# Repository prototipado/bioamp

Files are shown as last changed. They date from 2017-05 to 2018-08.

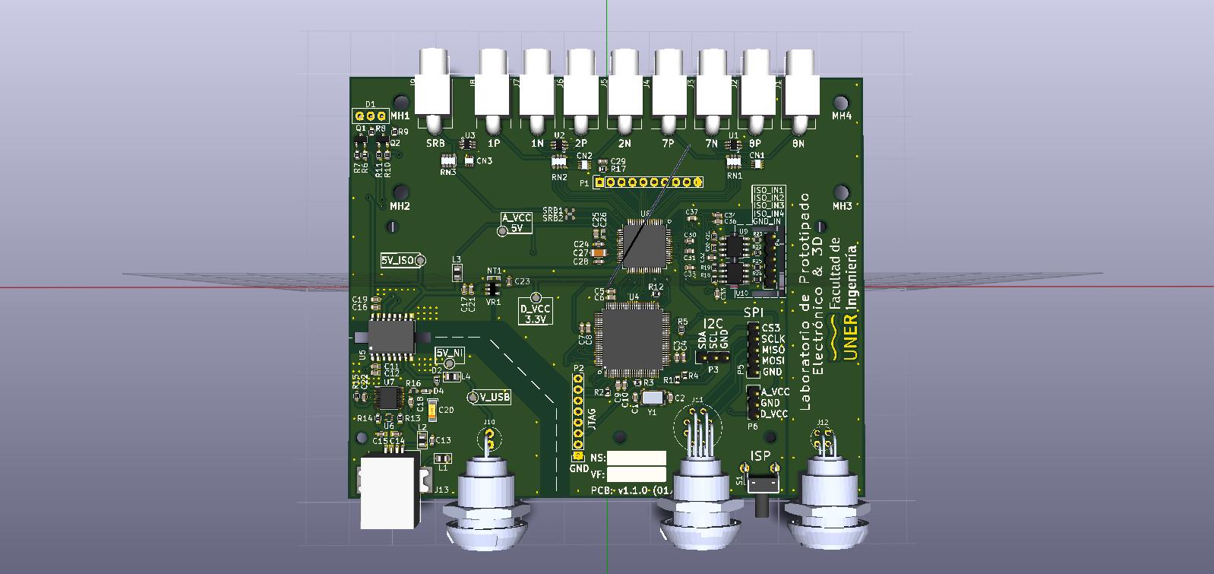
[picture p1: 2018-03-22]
Hardware/BioAmp_v1.1.0/images/BioAmp_v1.1.0_a.jpg

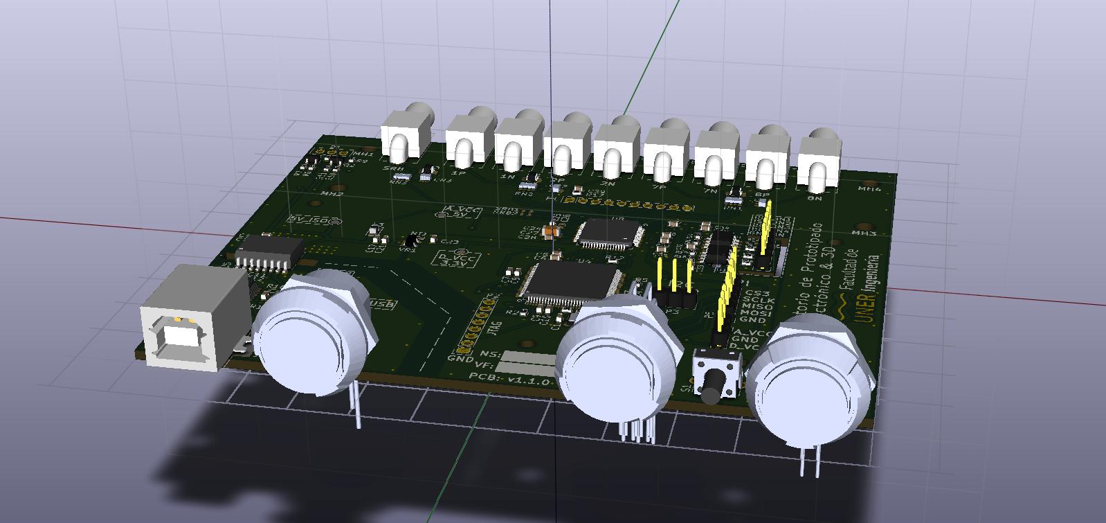
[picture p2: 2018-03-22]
Hardware/BioAmp_v1.1.0/images/BioAmp_v1.1.0_b.jpg

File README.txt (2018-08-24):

/****************************BioAmp Project**************************************************

Copyright 2017 - Laboratorio de Prototipado Electronico y 3D - FIUNER

Redistribution and use in source and binary forms, with or without modification, are permitted provided that the following conditions are met:

1. Redistributions of source code must retain the above copyright notice, this list of conditions and the following disclaimer.

2. Redistributions in binary form must reproduce the above copyright notice, this list of conditions and the following disclaimer in the documentation and/or other materials provided with the distribution.

3. Neither the name of the copyright holder nor the names of its contributors may be used to endorse or promote products derived from this design without specific prior written permission.

THIS DESING IS PROVIDED BY THE COPYRIGHT HOLDERS AND CONTRIBUTORS "AS IS" AND ANY EXPRESS OR IMPLIED WARRANTIES, INCLUDING, BUT NOT LIMITED TO, THE IMPLIED WARRANTIES OF MERCHANTABILITY AND FITNESS FOR A PARTICULAR PURPOSE ARE DISCLAIMED. IN NO EVENT SHALL THE COPYRIGHT HOLDER OR CONTRIBUTORS BE LIABLE FOR ANY DIRECT, INDIRECT, INCIDENTAL, SPECIAL, EXEMPLARY, OR CONSEQUENTIAL DAMAGES (INCLUDING, BUT NOT LIMITED TO, PROCUREMENT OF SUBSTITUTE GOODS OR SERVICES; LOSS OF USE, DATA, OR PROFITS; OR BUSINESS INTERRUPTION) HOWEVER CAUSED AND ON ANY THEORY OF LIABILITY, WHETHER IN CONTRACT, STRICT LIABILITY, OR TORT (INCLUDING NEGLIGENCE OR OTHERWISE) ARISING IN ANY WAY OUT OF THE USE OF THIS DESIGN, EVEN IF ADVISED OF THE POSSIBILITY OF SUCH DAMAGE.

/*
===============================================================================
 Initial Authors : 
		   Juan Ignacio Cerrudo (juanicerrudo@gmail.com) - Developer
		   Agustin Solano (asolano@gmail.com) - Developer
                   Eduardo Filomena (efilomena@ingenieria.uner.edu.ar) - Requirements Definition
		   Juan Manuel Reta (jmreta@ingenieria.uner.edu.ar ) - Project Manager
Colaborators:
		   Albano Peñalva (albanopenialva@gmail.com) - Developer
		   Christian Mista (cmista@ingenieria.uner.edu.ar) - Developer
===============================================================================
*/

BioAmp is an opensource project of a multichannel biopotential adquisition system for EEG, EMG, EOG and EOG signals.

The device has 8 programmable channels - 2000 Hz maximun sampling frequency, allowing the acquisition of biopotentials.

Features:

Resolution: 17 - 19 bits depending on settings (gain and sampling frequency).
Channels: 8 differential channels / 8 monopolar channels.
Input Impedance: ≥ 500 M Ω
Dimentions: 153x114x34mm

Laboratorio de Prototipado Electronico y 3D - FIUNER (http://ingenieria.uner.edu.ar/grupos/prototipado)
Laboratorio de Ingenierı́a en Rehabilitación e Investigaciones Neuromusculares y Sensoriales (LIRINS).

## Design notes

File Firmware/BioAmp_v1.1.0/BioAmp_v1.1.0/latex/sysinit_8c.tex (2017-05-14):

\hypertarget{sysinit_8c}{}\section{src/sysinit.c File Reference}
\label{sysinit_8c}\index{src/sysinit.\+c@{src/sysinit.\+c}}
{\ttfamily \#include \char`\"{}board.\+h\char`\"{}}\\*
\subsection*{Functions}
\begin{DoxyCompactItemize}
\item 
void \hyperlink{sysinit_8c_a93f514700ccf00d08dbdcff7f1224eb2}{System\+Init} (void)
\end{DoxyCompactItemize}

\subsection{Function Documentation}
\hypertarget{sysinit_8c_a93f514700ccf00d08dbdcff7f1224eb2}{}\index{sysinit.\+c@{sysinit.\+c}!System\+Init@{System\+Init}}
\index{System\+Init@{System\+Init}!sysinit.\+c@{sysinit.\+c}}
\subsubsection[{System\+Init(void)}]{\setlength{\rightskip}{0pt plus 5cm}void System\+Init (
\begin{DoxyParamCaption}
\item[{void}]{}
\end{DoxyParamCaption}
)}\label{sysinit_8c_a93f514700ccf00d08dbdcff7f1224eb2}

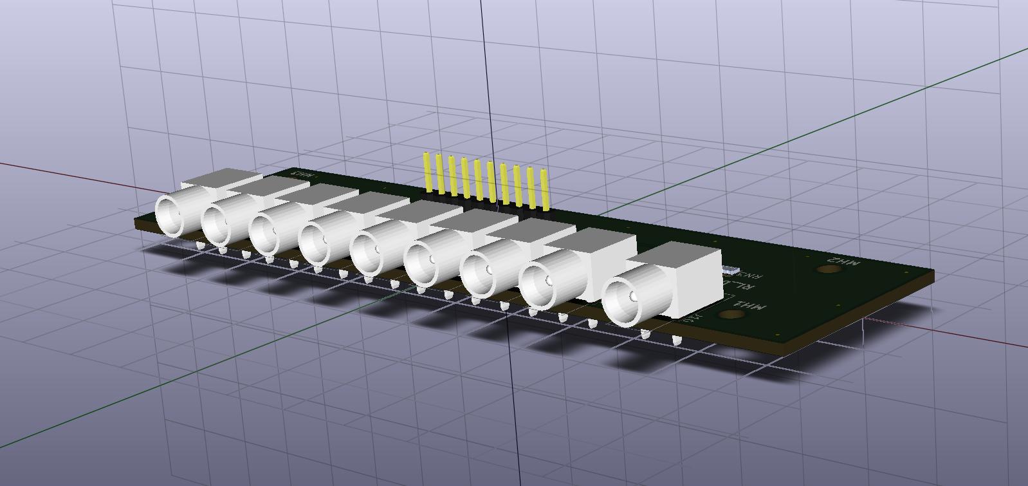
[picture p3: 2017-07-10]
Hardware/BioAmp_v1.1.0_DB/images/BioAmp_v1.0.0_DB_a.jpg

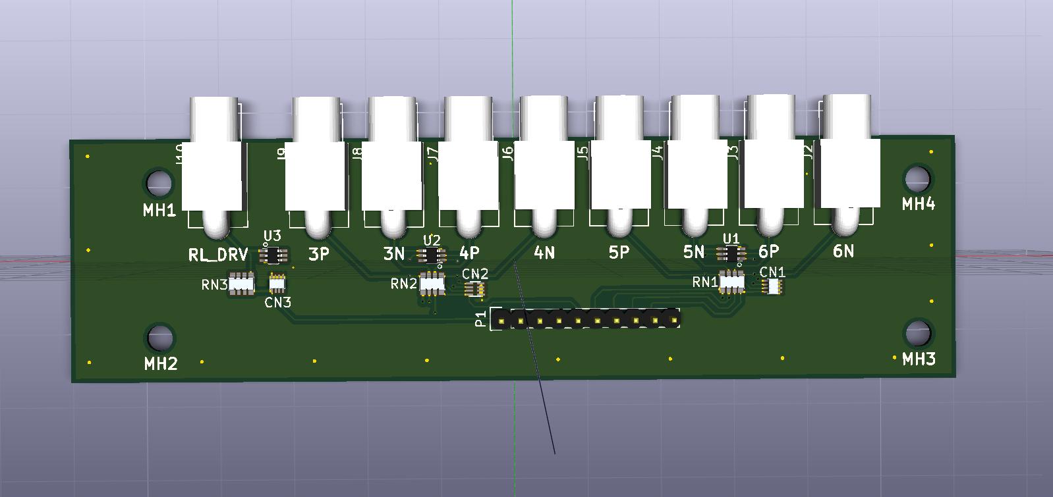
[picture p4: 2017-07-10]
Hardware/BioAmp_v1.1.0_DB/images/BioAmp_v1.0.0_DB_b.jpg

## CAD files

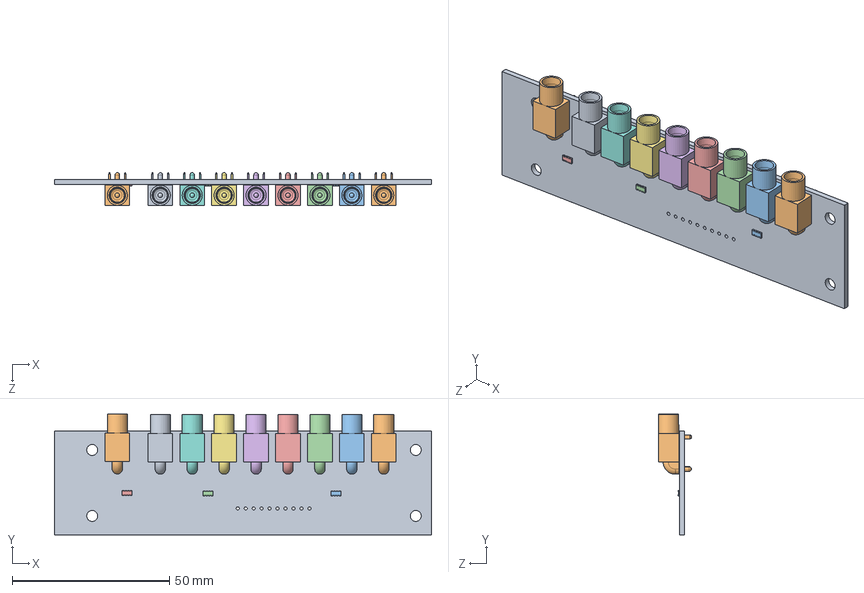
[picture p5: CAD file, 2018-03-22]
Hardware/3d_boards/BioAmp_v1.1.0_DB.SLDASM
120.0 x 38.4 x 10.4 mm
Board_outline_1
conector_touch-free__1
conector_touch-free_001_1
conector_touch-free_002_1
conector_touch-free_003_1
conector_touch-free_004_1
conector_touch-free_005_1
conector_touch-free_006_1
conector_touch-free_007_1
conector_touch-free_008_1
r_cay16-4__1
r_cay16-4_001_1
r_cay16-4_002_1

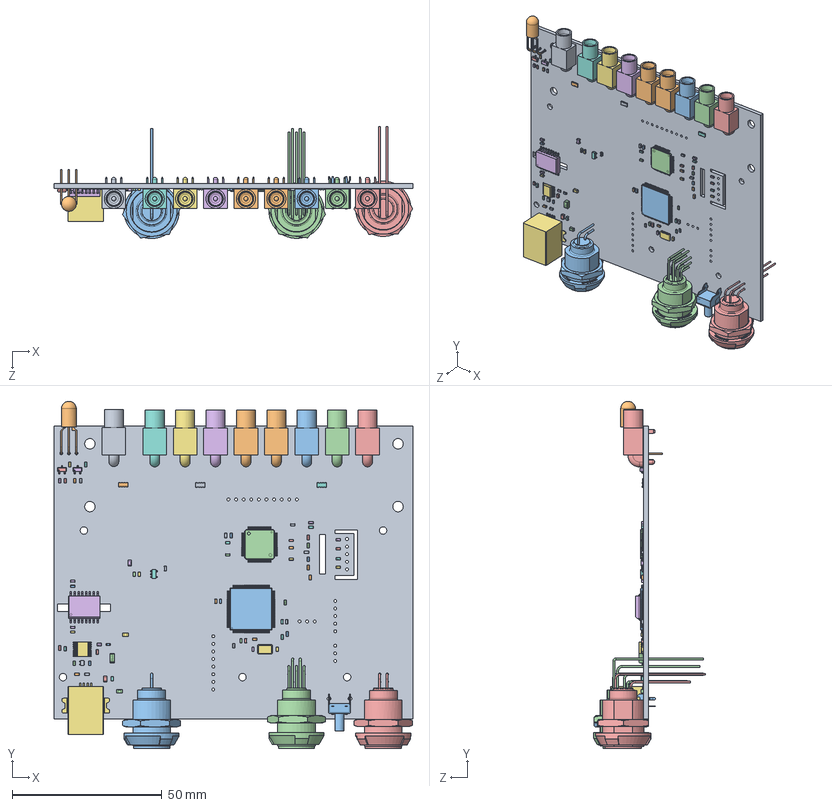
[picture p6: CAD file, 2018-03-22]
Hardware/3d_boards/BioAmp_v1.1.0.SLDASM
120.0 x 116.1 x 37.5 mm
Board_outline
conector_touch-free_
LQFP_100_14x14mm_Pitch0.5mm_
LQFP_64_10x10mm_Pitch0.5mm_
R_0603_
SOIC-16_7.5x10.3mm_Pitch1.27mm_
USB_B-smd_
C_0603_
C_0603_001
C_0603_002
C_0603_003
C_0603_004
C_0603_005
C_0603_006
C_0603_007
C_0603_008
C_0603_009
C_0603_010
C_0603_011
C_0603_012
C_0603_013
C_0603_014
C_0603_015
C_0603_016
C_0603_017
C_0603_018
C_0603_019
C_0603_020
C_0603_021
C_0603_022
C_0603_023
C_0603_024
C_0603_025
LED_TH_
LED_0603_
FER-0805_
FER-0805_001
FER-0805_002
FER-0805_003
R_0603_001
R_0603_002
R_0603_003
R_0603_004
R_0603_005
R_0603_006
R_0603_007
R_0603_008
R_0603_009
R_0603_010
R_0603_011
R_0603_012
R_0603_013
R_0603_014
R_0603_015
XTAL_AM3B_
r_cay16-4_
r_cay16-4_001
r_cay16-4_002
SW_Tactile_SPST_Angled_
c_tant_A_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

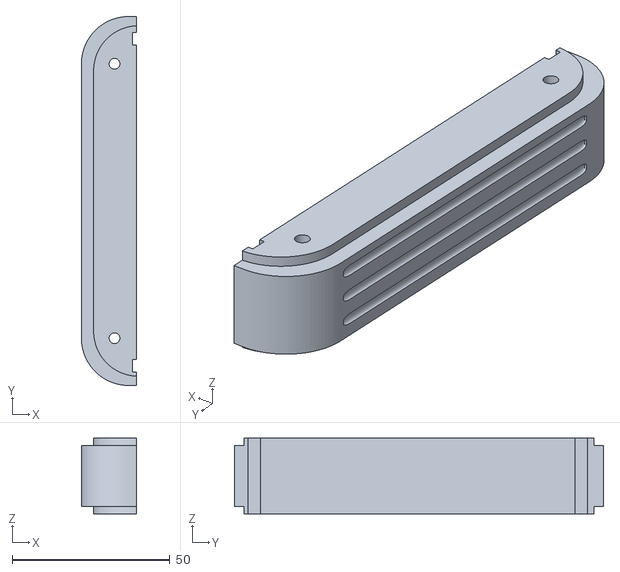
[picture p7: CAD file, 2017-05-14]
Enclosure/bioamp_body_right_1.0.stl
17.5 x 117.0 x 24.0

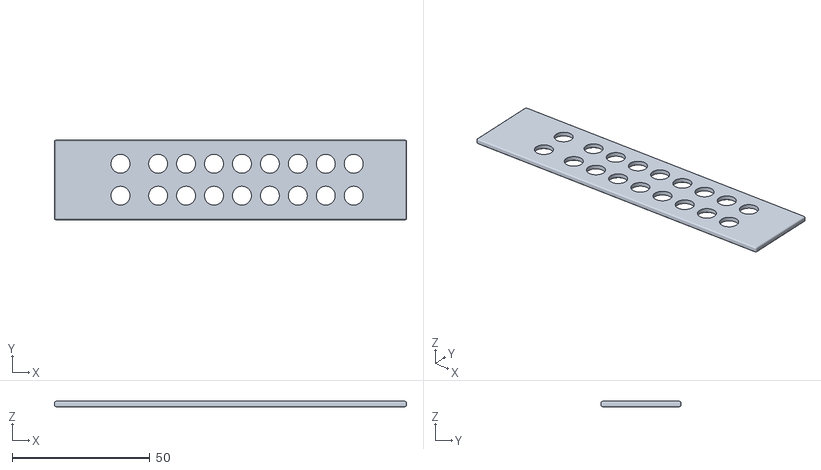
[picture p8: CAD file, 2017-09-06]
Enclosure/STL_1.2/bioamp_front_1.2.stl
128.0 x 29.0 x 2.00

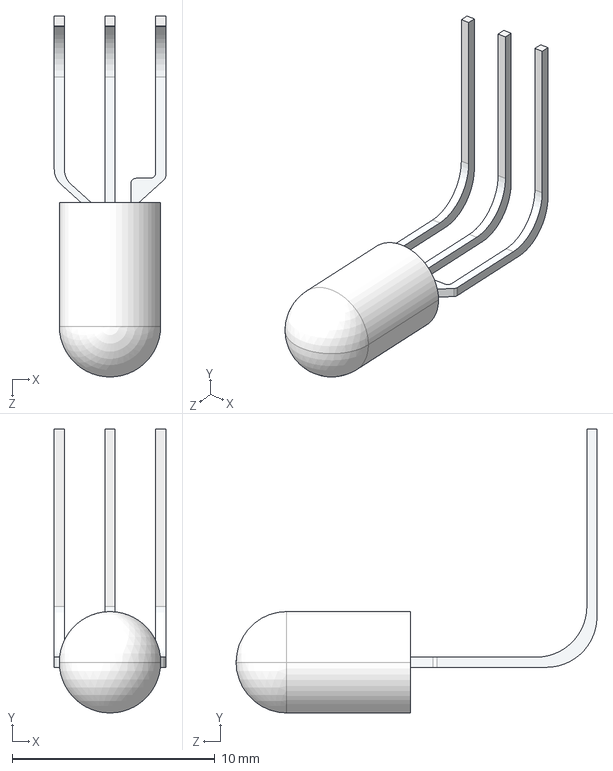
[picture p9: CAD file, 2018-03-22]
Hardware/BioAmp_v1.1.0/3d_models/LED_TH.STEP
5.50 x 14.0 x 17.8 mm

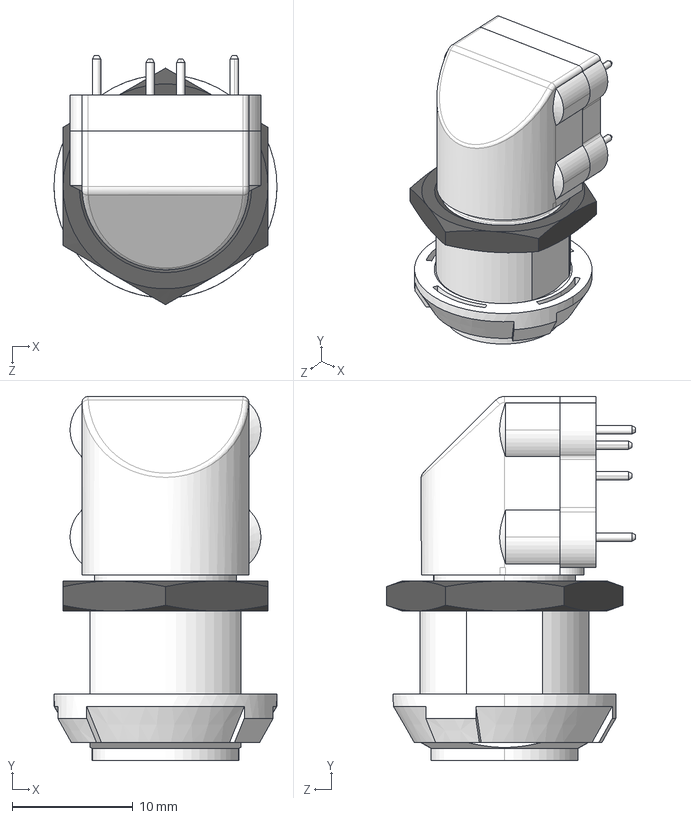
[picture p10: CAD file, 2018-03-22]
Hardware/BioAmp_v1.1.0_DB/3d_models/PXG.M0.4GG.NG.STEP
18.5 x 30.2 x 20.7 mm
pxg_m0_4gg_ng
pxg_m0_4gg_ng_2
pxg_m0_4gg_ng_3
pxg_m0_4gg_ng_4
pxg_m0_4gg_ng_5
pxg_m0_4gg_ng_6
pxg_m0_4gg_ng_7
pxg_m0_4gg_ng_8
pxg_m0_4gg_ng_9
pxg_m0_4gg_ng_10
pxg_m0_4gg_ng_11
pxg_m0_4gg_ng_12

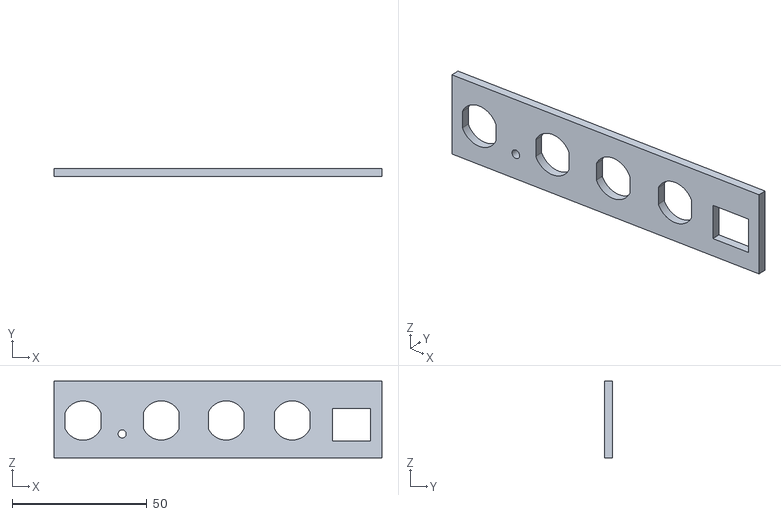
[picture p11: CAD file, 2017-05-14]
Enclosure/bioamp_back_1.0.stl
121.5 x 3.00 x 28.5

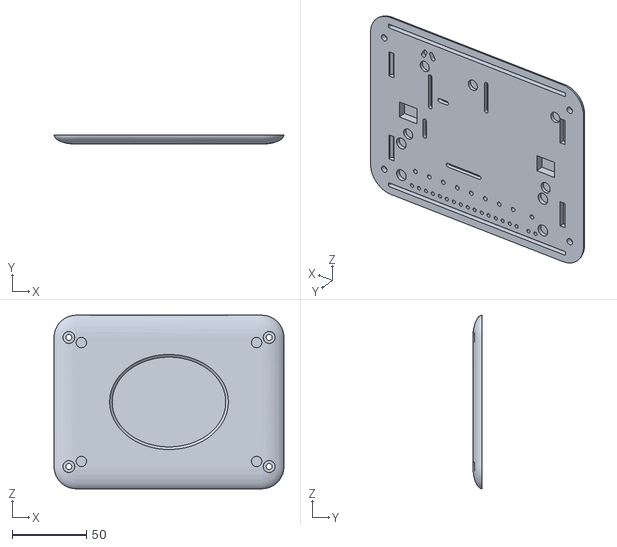
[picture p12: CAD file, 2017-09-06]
Enclosure/STL_1.2/bioamp_bottom_1.2.stl
155.0 x 6.25 x 117.0

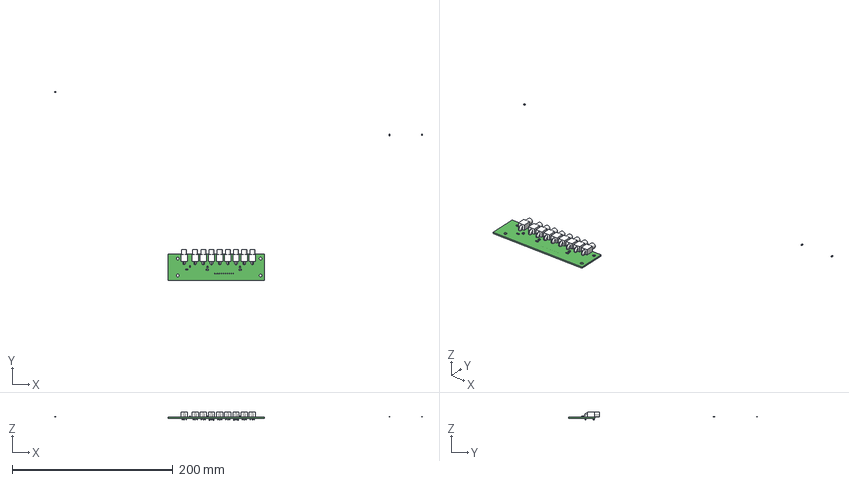
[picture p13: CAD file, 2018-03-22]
Hardware/3d_boards/BioAmp_v1_1_0_DB.FCStd
457.4 x 234.4 x 10.4 mm
Board_outline
r_cay16-4_
r_cay16-4_001
r_cay16-4_002
TSOP-6_2x1.25mm_Pitch0.65mm_
TSOP-6_2x1.25mm_Pitch0.65mm_001
Extruded_8_
Extruded_8_001
TSOP-6_2x1.25mm_Pitch0.65mm_002
Extruded_8_002
conector_touch-free_
conector_touch-free_001
conector_touch-free_002
conector_touch-free_003
conector_touch-free_004
conector_touch-free_005
conector_touch-free_006
conector_touch-free_007
conector_touch-free_008

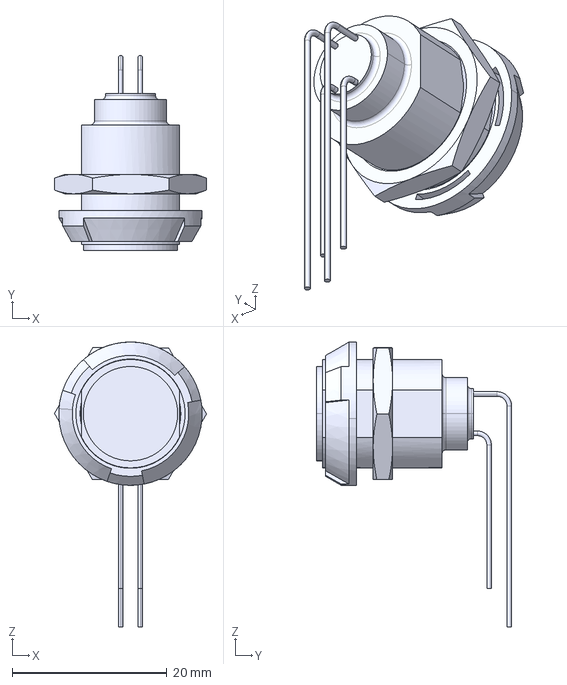
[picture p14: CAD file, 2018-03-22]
Hardware/BioAmp_v1.1.0/3d_models/PLB1G020004.step
19.6 x 25.2 x 36.8 mm

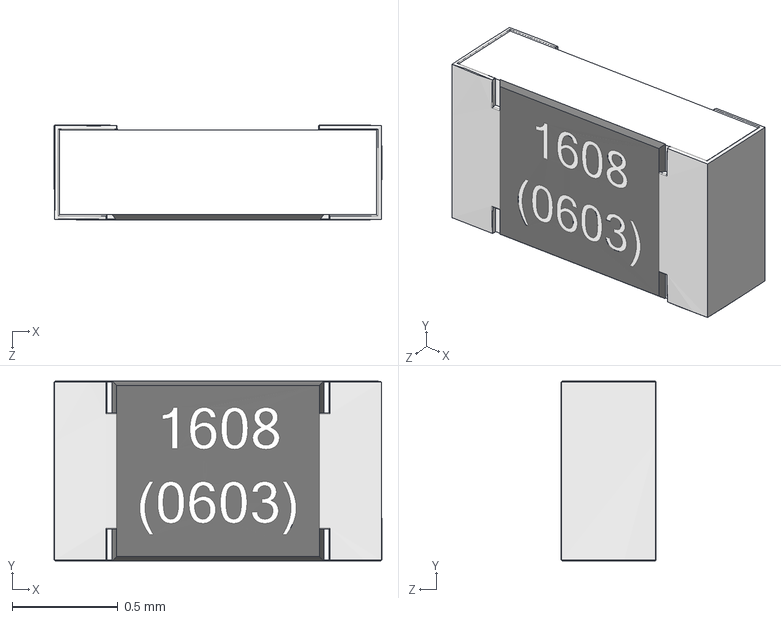
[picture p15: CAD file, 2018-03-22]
Hardware/BioAmp_v1.1.0_DB/3d_models/R_0603.STEP
1.55 x 0.85 x 0.451 mm

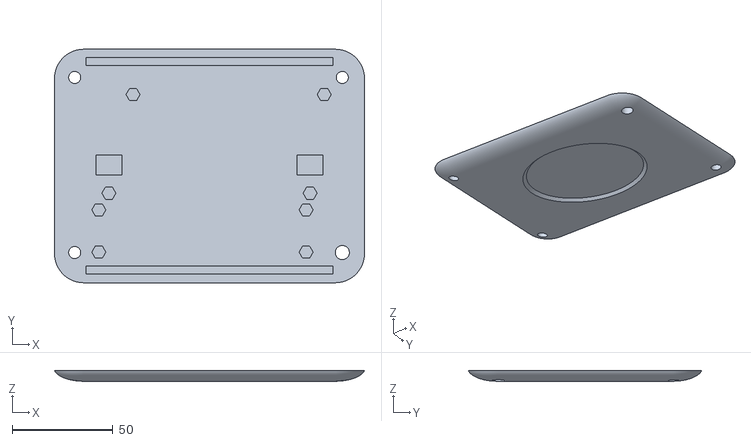
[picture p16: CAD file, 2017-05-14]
Enclosure/bioamp_bottom_1.0.stl
154.0 x 116.0 x 5.25

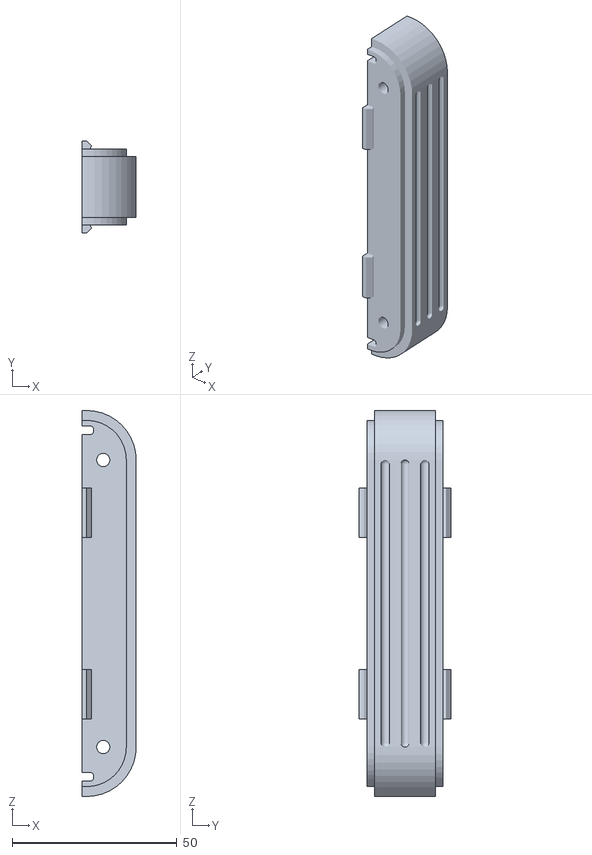
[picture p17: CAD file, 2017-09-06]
Enclosure/STL_1.2/bioamp_body_right_1.2.stl
16.5 x 28.0 x 117.0

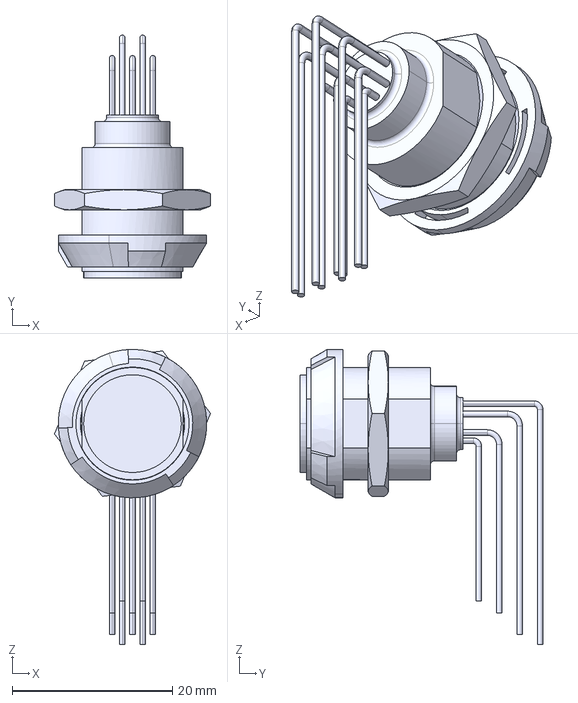
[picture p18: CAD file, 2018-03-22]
Hardware/BioAmp_v1.1.0/3d_models/PLB1G020010.step
19.5 x 30.3 x 36.8 mm

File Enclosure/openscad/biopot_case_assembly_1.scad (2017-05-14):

/**********************
Author: JM RETA
Project: Biopotencial Amplifier Case
Laboratorio de Prototipado Electrónico y 3D - FIUNER
02-2017

**********************/
//use <libs/nuts_and_bolts_v1.95.scad>;

$fn= 100;

/*Sphere  dimensions*/
X = 120;
Y = 75;
Z = 50;

sph_X = 100;
sph_Y = 80;
sph_Z = 60;
/*Dimension*/

X_i = 125;
Y_i = 85;//75
Z_i = 45;

/*Lateral Parameters*/

R_edges_v = 30; /*round radius for vertical edges*/
R_edges_h = 30; /*round radius for horizontal edges*/
thickness = 3;
/***Internal Hole***/

Xih = 120;
Yih = Y_i+R_edges_v;
Zih = 30;

/*******Grip Pattern*******/

G_DEEP = 0.3;
G_LONG = 80;
G_THICK = 1;
G_PITCH = 0.3;

/**************************/





/*Front panel*/
Xf = 120;
Yf = thickness-1;
Zf = 27;
R_border = 5;

border_thickness = 2.5;


/******Cuts**********/
Z_sph_cut =45;
Top_Part_Cut = R_edges_h/2-Z_i/2-3;
Bottom_Part_Cut = -R_edges_h/2-Z_i/2+3;
CUT = 1;
DRAW = 0;

/******Nuts Cuts*/
X_Border_Hole = 4.5;
Y_Border_Hole = 0;
Body_Nut_Heigth = 18;

/******Models***********/

sphere_top = 1;
boards_simulate = 0;
nuts_bolts=1;

GRIP_AND_CUTS = 1;

/*************************/
if(boards_simulate==1)
{
    color([0.3,0.8,0.5])
    {
        rotate([0,0,180])
        {
            translate([0,0,-9]) import("board.stl");
            translate([0,33,3])import("daugther_board.stl");
        }
    }
}

module grip_cylindrical (x_size, y_size, deep, pitch)
{
 
    //for ( i = [0 : pitch : (y_size-deep)/pitch] )
    for ( i = [0 : pitch : y_size] )
    {
        rotate( [90, 0, 0])
        {
            translate([0, 2*deep*20*i, 0]) minkowski()
            {
                cylinder(r = deep,h=x_size);
            resize(newsize=[deep,3*deep,10*deep])sphere(r=deep);
            }
        }
    }
}

module lateral(xl,yl,zl,r_edge_v,r_edge_h)
{
       minkowski()
       {
            cube([xl,yl,zl/2],center = true);
            resize(newsize=[r_edge_v,r_edge_h,14]) sphere(r_edge_v);
        }
}
module lateral_border(xl,yl,z,r_edge_v,r_edge_h)
{
difference()
{
lateral(xl,yl,z,r_edge_v,r_edge_h);
scale([0.95,0.95,0.95]) 
{
 lateral(xl,yl,z,r_edge_v,r_edge_h);
}
/*solids for substraction*/

 translate([0,0,Z_i/2])cube([2*X,2*Y,Z_i],center=true);
 translate([0,0,-Z_i/2-border_thickness])cube([2*X,2*Y,Z_i],center=true);
 }

/******/
 }
 module top_part()
 {
union()
{
        difference()
  //intersection()   
        {  
          union()
          {
//                hull()
//              {  
              lateral(X_i, Y_i, Z_i,R_edges_v,R_edges_h);
                if(sphere_top==1)
                {
                  difference()
                    {
                        resize(newsize=[sph_X,sph_Y,sph_Z]) sphere(r=20);
                /*sphere cut*/
                        translate ([0,0,Z_sph_cut])cube([X,Y,Z], center = true);  
                    }
 //               }
            }
            }
                //translate([0,0,0])
                translate([0,0,Top_Part_Cut ])cube([2*X_i,2*Y_i,Z_i],center=true);  
                front_part(CUT);
                back_part(CUT);
        }
    }
}
module body_part()
{
    difference()
    {
        intersection()
        {
            difference()
            {
               lateral(X_i, Y_i, Z_i,R_edges_v,R_edges_h);
               translate([0,0,-Top_Part_Cut+1.7])          lateral_border(X_i, Y_i, Z_i,R_edges_v,R_edges_h);
               translate([0,0,Bottom_Part_Cut/2+7.6])lateral_border(X_i, Y_i, Z_i,R_edges_v,R_edges_h);
               translate([0,0,-1]) cube([Xih,Yih+20,Zih],center=true);
//               #translate([0,0,-1]) cube([X_i, Y_i+R_edges_v, Z_i],center=true);
            }
      translate([0,0,Top_Part_Cut])cube([2*X_i,2*Y_i,Z_i],center=true);
        }
        translate([0,0,Bottom_Part_Cut])cube([2*X_i,2*Y_i,Z_i],center=true); 
        
    translate ([-X_i/2-X_Border_Hole, -Y_i/2-Y_Border_Hole, -20]) cylinder(r=3,Body_Nut_Heigth,$fn=6);
    translate ([-X_i/2-X_Border_Hole, Y_i/2-Y_Border_Hole, -20]) cylinder(r=3,Body_Nut_Heigth,$fn=6);
    translate ([X_i/2-X_Border_Hole+8, -Y_i/2-Y_Border_Hole, -20]) cylinder(r=3,Body_Nut_Heigth,$fn=6);
    translate ([X_i/2-X_Border_Hole+8, Y_i/2-Y_Border_Hole, -20]) cylinder(r=3,Body_Nut_Heigth,$fn=6);
        
    if(GRIP_AND_CUTS == 1)
    {
            front_part(CUT);
            back_part(CUT);
           translate([-X_i/2-15,G_LONG/2,-5.5])grip_cylindrical (G_LONG, G_THICK, G_DEEP, G_PITCH);
            translate([X_i/2+15,G_LONG/2,-5.5])grip_cylindrical (G_LONG, G_THICK, G_DEEP, G_PITCH);
    }
   }
}
module bottom_part()
{
    X_Board_Hole1 = 57;
    Y_Board_Hole1 = 35;
    
    X_Board_Hole2 = -38;
    Y_Board_Hole2 = 35;
    
    X_Board_Hole3 = -50;
    Y_Board_Hole3 = -14;
    
    X_Board_Hole4 = 50;
    Y_Board_Hole4 = -14;
    
    Z_Board_Hole = -16;
    
    Board_Nut_Heigth = 3.5;
    
 difference()
    {
union()
    {
        intersection()
        {
                lateral(X_i, Y_i, Z_i,R_edges_v,R_edges_h);
            translate([0,0,Bottom_Part_Cut-1])cube([2*X_i,2*Y_i,Z_i],center=true);
        }    
    }
    /****Front and Back panels cuts************/
    
    front_part(CUT);
    back_part(CUT);
    
    
    /****Cuts screws side by side***/
      translate([0,0,-Z_i+8])top_part();
    translate ([-X_i/2-X_Border_Hole, -Y_i/2-Y_Border_Hole, -20]) cylinder(r=1.5,Body_Nut_Heigth);
    translate ([-X_i/2-X_Border_Hole, Y_i/2-Y_Border_Hole, -20]) cylinder(r=1.5,Body_Nut_Heigth);
    translate ([X_i/2-X_Border_Hole+8, -Y_i/2-Y_Border_Hole, -20]) cylinder(r=1.5,Body_Nut_Heigth);
    translate ([X_i/2-X_Border_Hole+8, Y_i/2-Y_Border_Hole, -20]) cylinder(r=1.5,Body_Nut_Heigth);
    
    /***Cuts screws heads**/
    translate([0,0,-Z_i+8])top_part();
    translate ([-X_i/2-X_Border_Hole, -Y_i/2-Y_Border_Hole, -20]) cylinder(r=3,h=Body_Nut_Heigth/3.5);
    translate ([-X_i/2-X_Border_Hole, Y_i/2-Y_Border_Hole, -20]) cylinder(r=3,h=Body_Nut_Heigth/3.5);
    translate ([X_i/2-X_Border_Hole+8, -Y_i/2-Y_Border_Hole, -20]) cylinder(r=3,h=Body_Nut_Heigth/3.5);
    translate ([X_i/2-X_Border_Hole+8, Y_i/2-Y_Border_Hole, -20]) cylinder(r=3,h=Body_Nut_Heigth/3.5);

        /*****Board Nuts Cuts******/

     translate ([X_Board_Hole1, Y_Board_Hole1, Z_Board_Hole]) cylinder(r=3,Board_Nut_Heigth,$fn=6);
     translate ([X_Board_Hole2, Y_Board_Hole2, Z_Board_Hole]) cylinder(r=3,Board_Nut_Heigth,$fn=6);
     translate ([X_Board_Hole3, Y_Board_Hole3, Z_Board_Hole]) cylinder(r=3,Board_Nut_Heigth,$fn=6);
     translate ([X_Board_Hole4, Y_Board_Hole4, Z_Board_Hole]) cylinder(r=3,Board_Nut_Heigth,$fn=6);
    }
}

module front_part(for_cut)
{  
    X_Hole1 = 44.8;
    X_Hole2 = 57;
    Y_Hole1 = 5.5;
     Y_Hole2 = -6.5;
    Z_Hole1 = 50;
    Z_Hole2 = 50;
    
    X_cover_led = 55;
    Y_cover_led = -3.5;
    Z_cover_led = 47.5;
    
   if(for_cut ==1)
         {
           translate ([0,-(Yih/2-Yf-R_border/2-1.7),0])
             minkowski(){
            cube([Xf,Yf-1.5,Zf-R_border+2],center = true);
            rotate([90,0,0])cylinder(r=R_border/2,Yf+1);
            }
         }else
         {
           difference(){
               union(){
           translate ([0,-(Yih/2-Yf-R_border/2-2),0])
           minkowski(){
           cube([Xf,Yf-1.9,Zf-R_border+1],center = true);
           rotate([90,0,0])cylinder(r=R_border/2,Yf+1);
         }
                    /*led cover*/    
           difference()
           {
                rotate([90,0,0]) translate([X_cover_led,Y_cover_led,Z_cover_led]) cylinder(r=5,h=4);
                rotate([90,0,0]) translate([X_cover_led,  Y_cover_led,Z_cover_led]) cylinder(r=2.6,h=5);
           }
       }
       
       #rotate([90,0,0]) translate([X_cover_led,  Y_cover_led,Z_cover_led-1]) cylinder(r=3.5,h=5);
       
           difference(){
           rotate([90,0,0]) translate([X_cover_led,Y_cover_led,Z_cover_led+5.5]) cylinder(r=3.5,h=4);
           rotate([90,0,0]) translate([X_cover_led,  Y_cover_led,Z_cover_led+5.5]) cylinder(r=2.7,h=4);
           }
           
        for(i=[0:7]) {
        rotate([90,0,0]) translate([-X_Hole1+i*10.16,-Y_Hole1,Z_Hole1]) cylinder(r=3.8,h=6);
        }
        rotate([90,0,0]) translate([-X_Hole1+8*10+4.8,-Y_Hole1,Z_Hole1]) cylinder(r=3.8,h=6);     
        for(j=[0:7]) {
      rotate([90,0,0]) translate([-X_Hole1+j*10.16,-Y_Hole2,Z_Hole2]) cylinder(r=3.8,h=6);
        }
      rotate([90,0,0]) translate([-X_Hole1+8*10+4.8,-Y_Hole2,Z_Hole1]) cylinder(r=3.8,h=6);
      /*led cover*/        
        }
     }
}
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

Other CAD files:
Hardware/BioAmp_v1.1.0_DB/3d_models/PXG.M0.2GG.NG.STEP
Enclosure/bioamp_body_left_1.0.stl
Enclosure/STL_1.2/bioamp_back_1.2.stl
Hardware/BioAmp_v1.1.0/3d_models/led_bicolor.step
Enclosure/STL_1.2/bioamp_body_left_1.2.stl
Enclosure/STL_1.2/bioamp_standoff.STL
Enclosure/STL_1.2/bioamp_top_1.2.STL
Enclosure/STL_1.2/bioamp_top_UNER_1.2.STL
Enclosure/bioamp_front_1.0.stl
Enclosure/bioamp_top_1.0.stl
Hardware/BioAmp_v1.1.0/3d_models/C_0603.STEP
Hardware/BioAmp_v1.1.0/3d_models/Cap_Array_4.STEP
Hardware/BioAmp_v1.1.0/3d_models/FER-0805.STEP
Hardware/BioAmp_v1.1.0/3d_models/Jack_TouchProof_1.5mm.STEP
Hardware/BioAmp_v1.1.0/3d_models/LED_0603.STEP
Hardware/BioAmp_v1.1.0/3d_models/PLB1G020002.STEP
Hardware/BioAmp_v1.1.0/3d_models/R_0603.STEP
Hardware/BioAmp_v1.1.0/3d_models/SOIC-16_7.5x10.3mm_Pitch1.27mm.STEP
Hardware/BioAmp_v1.1.0/3d_models/SOIC-8_3.9x4.9mm_Pitch1.27mm.step
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

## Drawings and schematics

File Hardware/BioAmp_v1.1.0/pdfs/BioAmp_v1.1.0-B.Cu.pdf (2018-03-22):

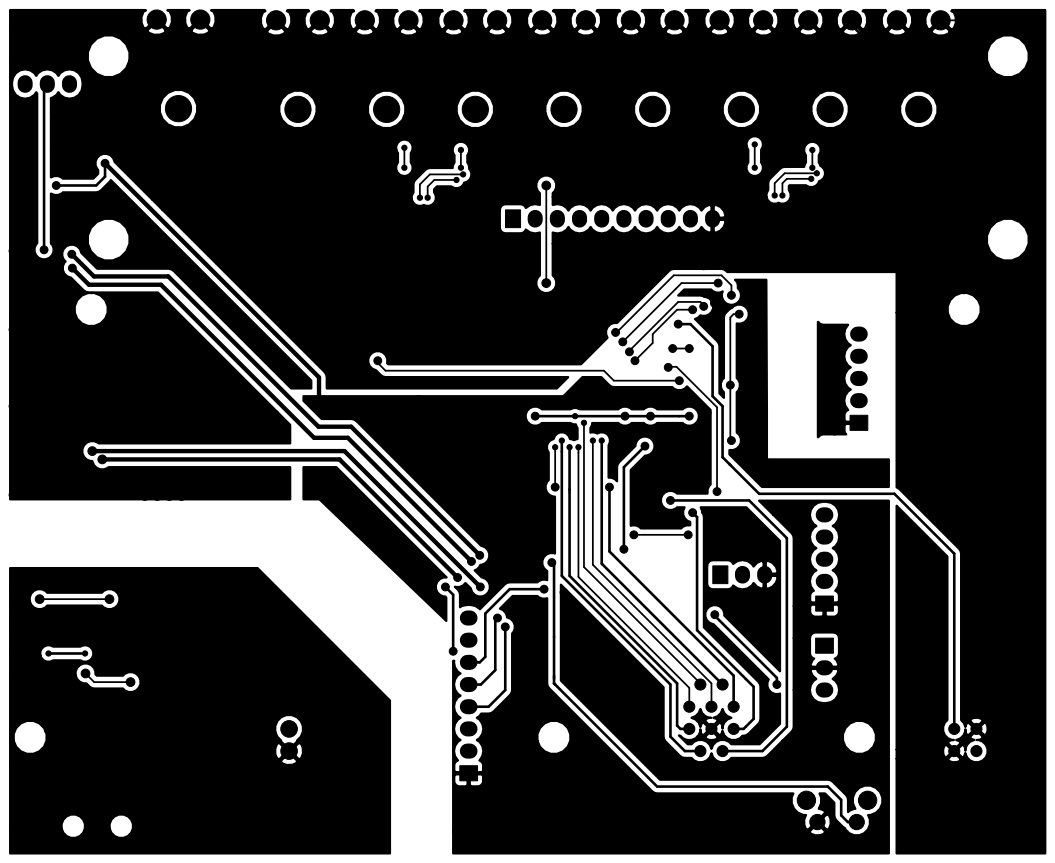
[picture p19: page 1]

File: BioAmp_v1.1.0.kicad_pcb Sheet:
Id: 1/1 Title: BioAmp-FIUNER-Lab. de Prototipado

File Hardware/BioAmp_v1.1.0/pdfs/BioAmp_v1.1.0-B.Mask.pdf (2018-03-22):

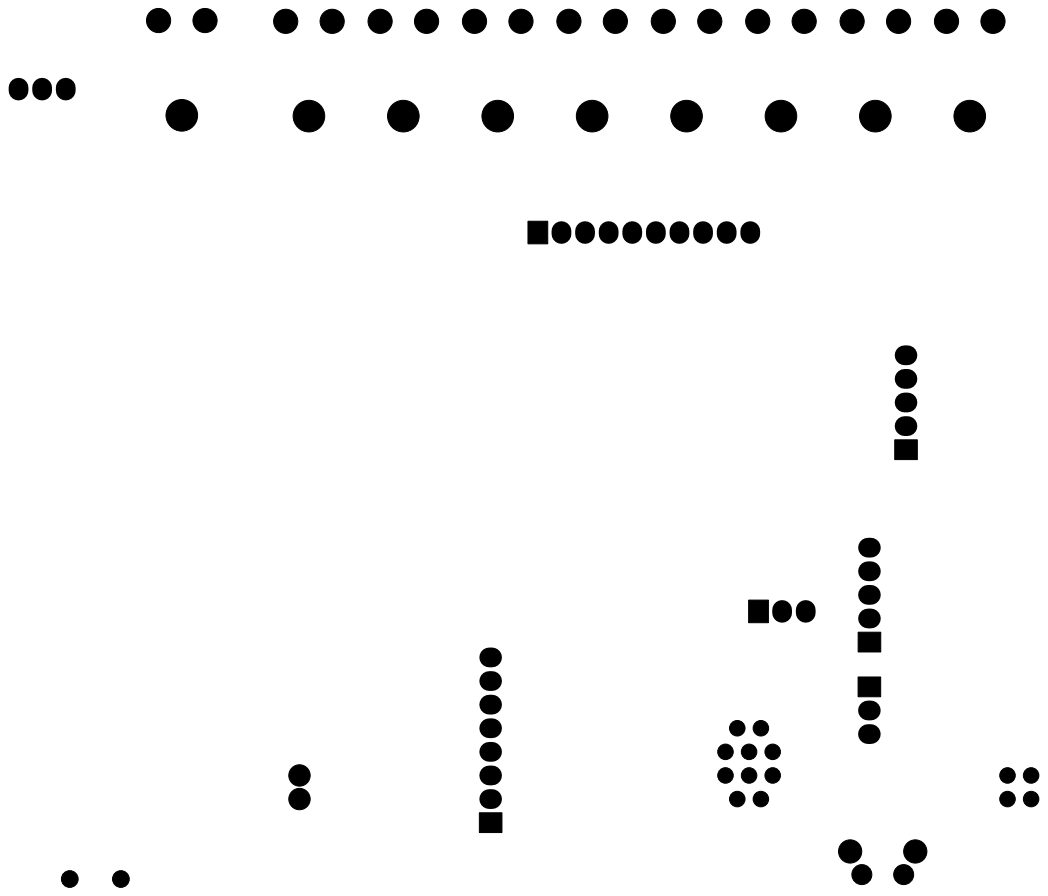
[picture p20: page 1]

File: BioAmp_v1.1.0.kicad_pcb Sheet:
Id: 1/1 Title: BioAmp-FIUNER-Lab. de Prototipado

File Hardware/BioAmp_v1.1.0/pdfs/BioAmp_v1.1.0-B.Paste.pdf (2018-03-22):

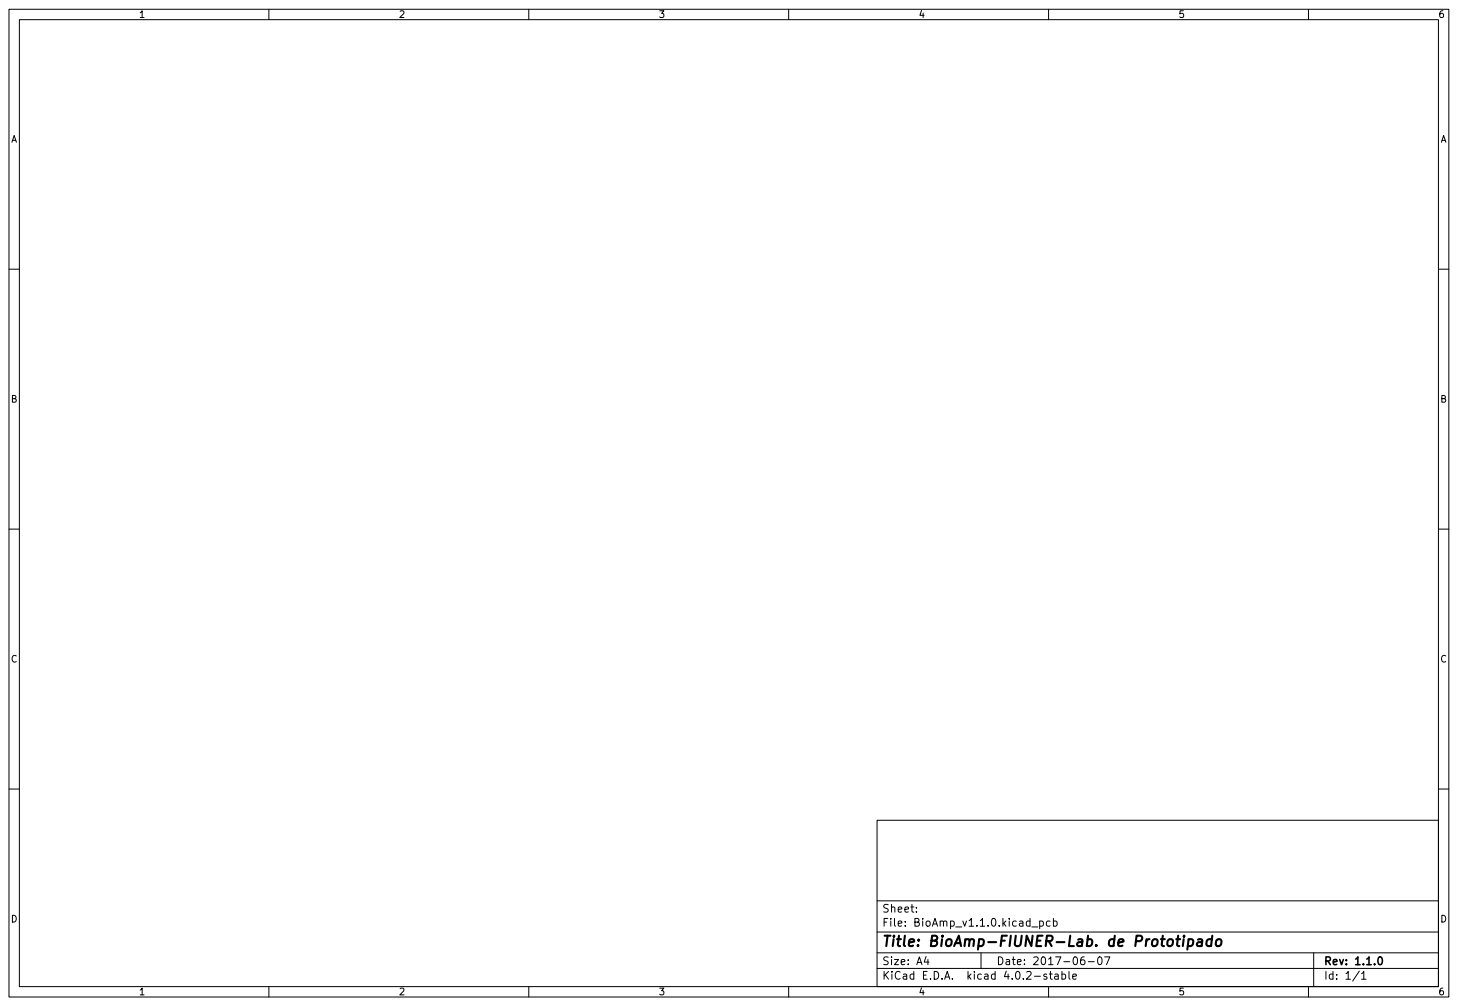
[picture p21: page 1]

File: BioAmp_v1.1.0.kicad_pcb Sheet:
Id: 1/1 Title: BioAmp-FIUNER-Lab. de Prototipado

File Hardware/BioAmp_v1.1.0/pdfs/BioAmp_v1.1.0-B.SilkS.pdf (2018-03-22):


File: BioAmp_v1.1.0.kicad_pcb Sheet:
Id: 1/1 Title: BioAmp-FIUNER-Lab. de Prototipado

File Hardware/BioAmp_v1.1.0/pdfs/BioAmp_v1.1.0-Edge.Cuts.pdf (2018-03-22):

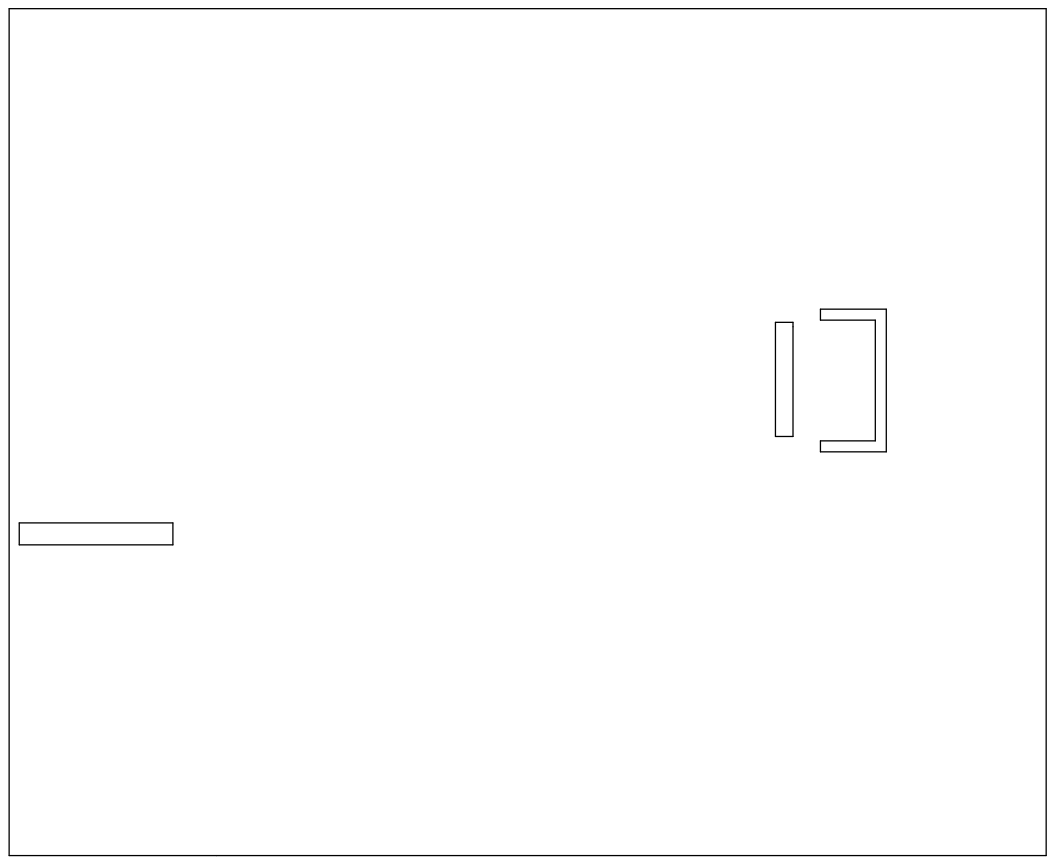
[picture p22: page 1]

File: BioAmp_v1.1.0.kicad_pcb Sheet:
Id: 1/1 Title: BioAmp-FIUNER-Lab. de Prototipado

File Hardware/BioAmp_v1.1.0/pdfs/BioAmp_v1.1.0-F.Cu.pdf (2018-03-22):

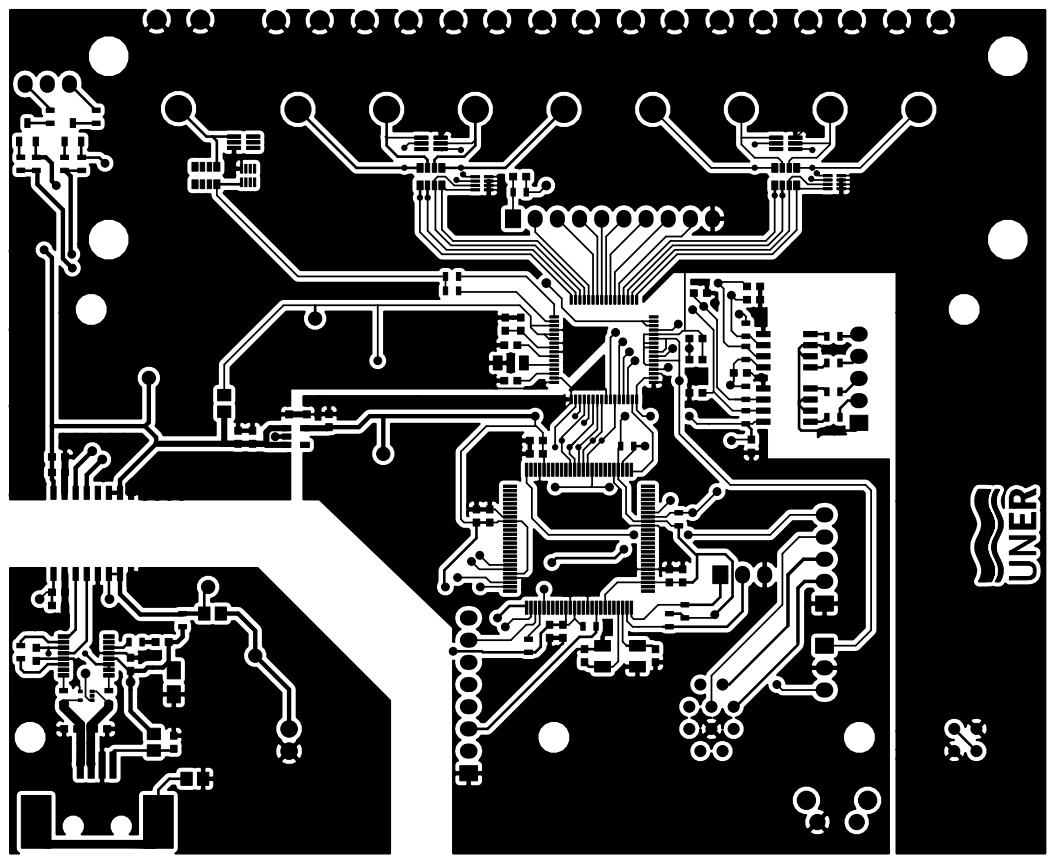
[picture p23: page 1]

File: BioAmp_v1.1.0.kicad_pcb Sheet:
Id: 1/1 Title: BioAmp-FIUNER-Lab. de Prototipado

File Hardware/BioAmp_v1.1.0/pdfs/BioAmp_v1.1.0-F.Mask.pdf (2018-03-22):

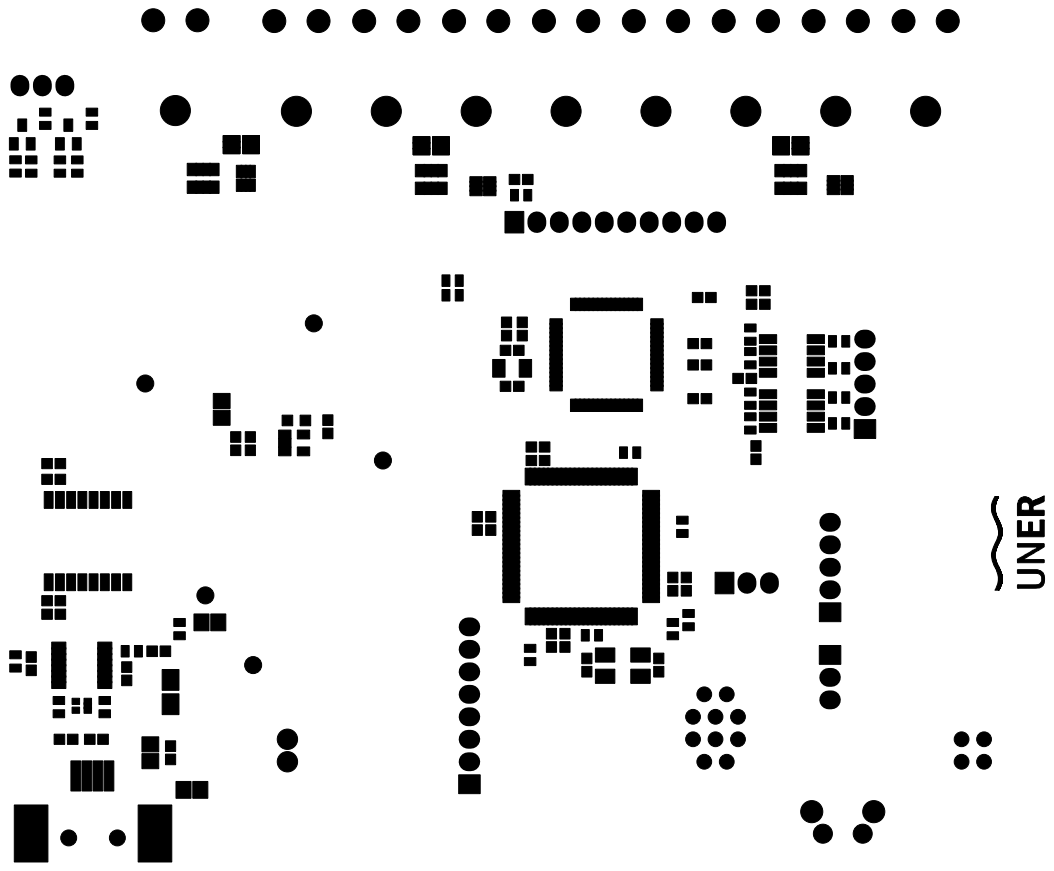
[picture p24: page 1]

File: BioAmp_v1.1.0.kicad_pcb Sheet:
Id: 1/1 Title: BioAmp-FIUNER-Lab. de Prototipado

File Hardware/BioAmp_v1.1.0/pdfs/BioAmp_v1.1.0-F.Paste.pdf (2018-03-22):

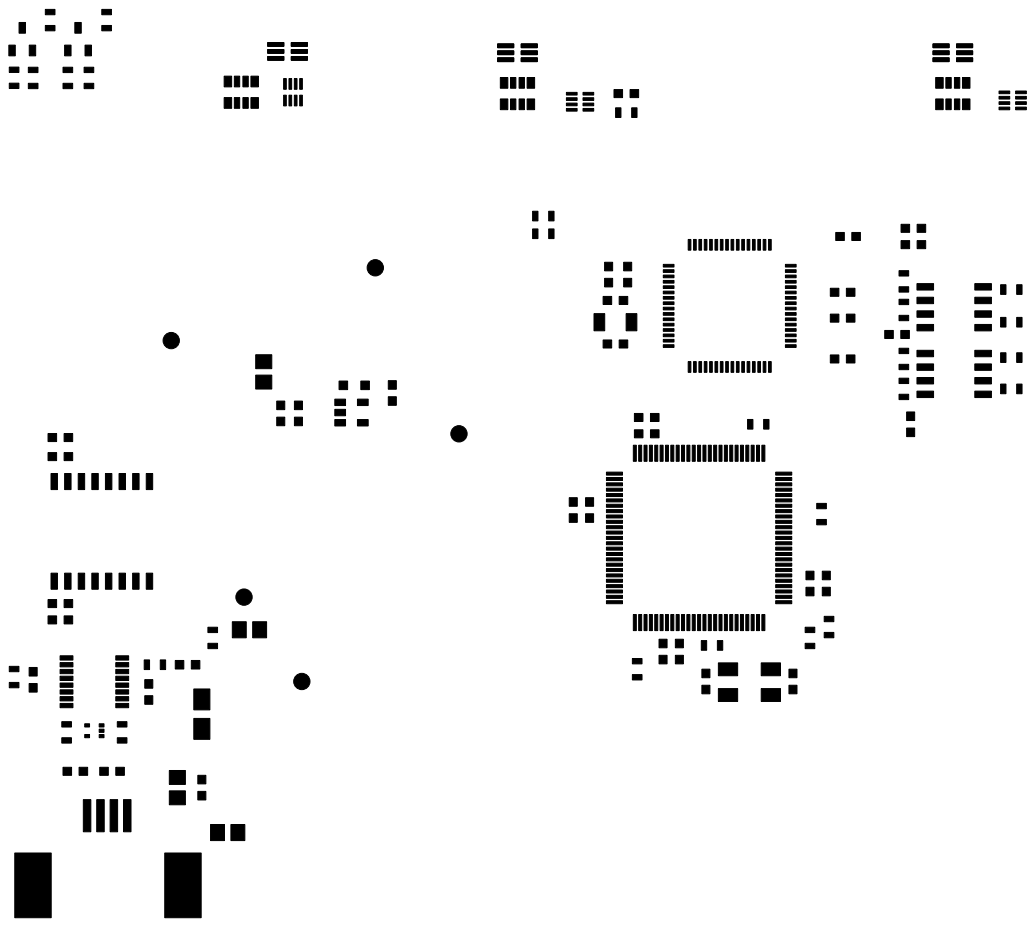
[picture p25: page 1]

File: BioAmp_v1.1.0.kicad_pcb Sheet:
Id: 1/1 Title: BioAmp-FIUNER-Lab. de Prototipado

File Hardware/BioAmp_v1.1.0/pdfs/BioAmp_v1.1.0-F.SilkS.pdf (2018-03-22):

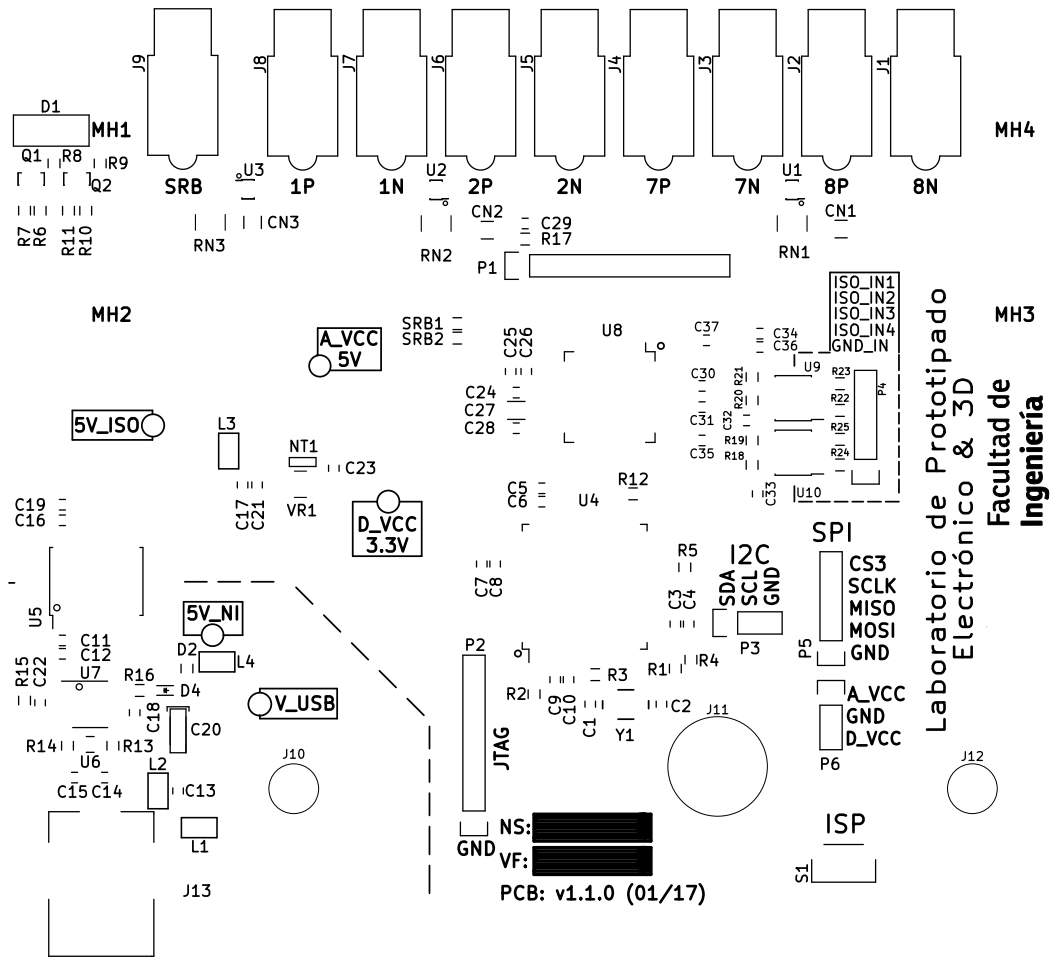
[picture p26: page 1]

CS3 SCLK MISO MOSI SDA SCL GND

Id: 1/1 Title: BioAmp-FIUNER-Lab. de Prototipado

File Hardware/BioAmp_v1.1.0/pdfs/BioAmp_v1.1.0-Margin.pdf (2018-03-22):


File: BioAmp_v1.1.0.kicad_pcb Sheet:
Id: 1/1 Title: BioAmp-FIUNER-Lab. de Prototipado

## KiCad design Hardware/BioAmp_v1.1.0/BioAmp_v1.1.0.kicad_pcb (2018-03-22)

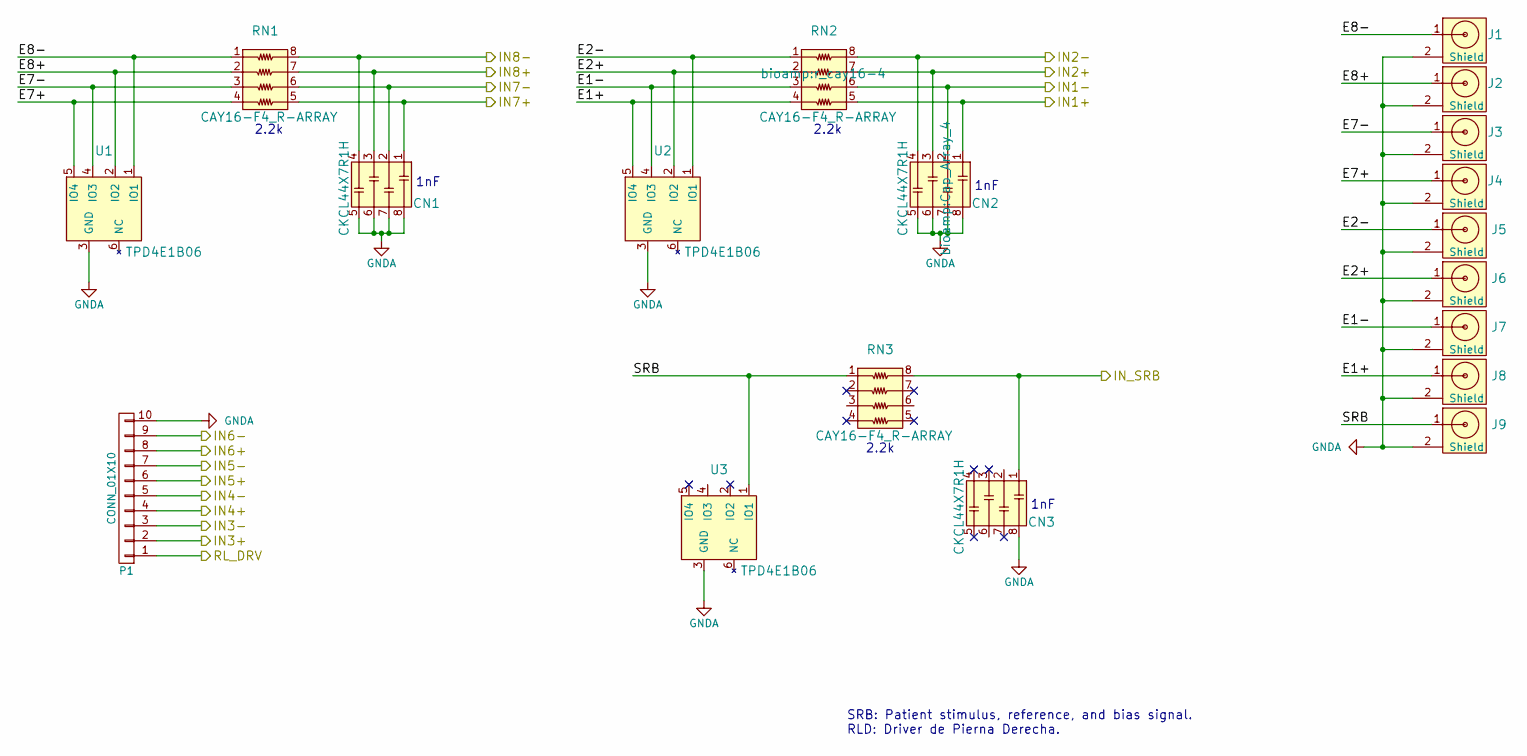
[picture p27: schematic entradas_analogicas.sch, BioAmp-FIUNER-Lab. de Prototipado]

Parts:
CN1, CN2, CN3: CKCL44X7R1H; Cap_Array_4
J1, J2, J3, J4, J5, J6, J7, J8, J9: Jack_Touch-Proof; Jack_TouchProof_1.5mm
P1: CONN_01X10; Pin_Header_Straight_1x10
RN1, RN2, RN3: CAY16-F4_R-ARRAY; r_cay16-4
U1, U2, U3: TPD4E1B06; TSOP-6_2x1.25mm_Pitch0.65mm

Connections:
/Analog Front End/RL_DRV: P1.1; also elsewhere on the board
/Entradas Analogicas/E1+: J8.1, RN2.4, U2.5 (IO4)
/Entradas Analogicas/E1-: J7.1, RN2.3, U2.4 (IO3)
/Entradas Analogicas/E2+: J6.1, RN2.2, U2.2 (IO2)
/Entradas Analogicas/E2-: J5.1, RN2.1, U2.1 (IO1)
/Entradas Analogicas/E7+: J4.1, RN1.4, U1.5 (IO4)
/Entradas Analogicas/E7-: J3.1, RN1.3, U1.4 (IO3)
/Entradas Analogicas/E8+: J2.1, RN1.2, U1.2 (IO2)
/Entradas Analogicas/E8-: J1.1, RN1.1, U1.1 (IO1)
/Entradas Analogicas/IN1+: CN2.1, RN2.5; also elsewhere on the board
/Entradas Analogicas/IN1-: CN2.2, RN2.6; also elsewhere on the board
/Entradas Analogicas/IN2+: CN2.3, RN2.7; also elsewhere on the board
/Entradas Analogicas/IN2-: CN2.4, RN2.8; also elsewhere on the board
/Entradas Analogicas/IN3+: P1.2; also elsewhere on the board
/Entradas Analogicas/IN3-: P1.3; also elsewhere on the board
/Entradas Analogicas/IN4+: P1.4; also elsewhere on the board
/Entradas Analogicas/IN4-: P1.5; also elsewhere on the board
/Entradas Analogicas/IN5+: P1.6; also elsewhere on the board
/Entradas Analogicas/IN5-: P1.7; also elsewhere on the board
/Entradas Analogicas/IN6+: P1.8; also elsewhere on the board
/Entradas Analogicas/IN6-: P1.9; also elsewhere on the board
/Entradas Analogicas/IN7+: CN1.1, RN1.5; also elsewhere on the board
/Entradas Analogicas/IN7-: CN1.2, RN1.6; also elsewhere on the board
/Entradas Analogicas/IN8+: CN1.3, RN1.7; also elsewhere on the board
/Entradas Analogicas/IN8-: CN1.4, RN1.8; also elsewhere on the board
/Entradas Analogicas/IN_SRB: CN3.1, RN3.8; also elsewhere on the board
/Entradas Analogicas/SRB: J9.1, RN3.1, U3.1 (IO1)
GNDA: CN1.5, CN1.6, CN1.7, CN1.8, CN2.5, CN2.6, CN2.7, CN2.8, CN3.8, J1.2 (Shield), J2.2 (Shield), J3.2 (Shield), J4.2 (Shield), J5.2 (Shield), J6.2 (Shield), J7.2 (Shield), J8.2 (Shield), J9.2 (Shield), P1.10, U1.3 (GND), U2.3 (GND), U3.3 (GND); also elsewhere on the board

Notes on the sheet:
SRB: Patient stimulus, reference, and bias signal. RLD: Driver de Pierna Derecha.
2.2k
1nF

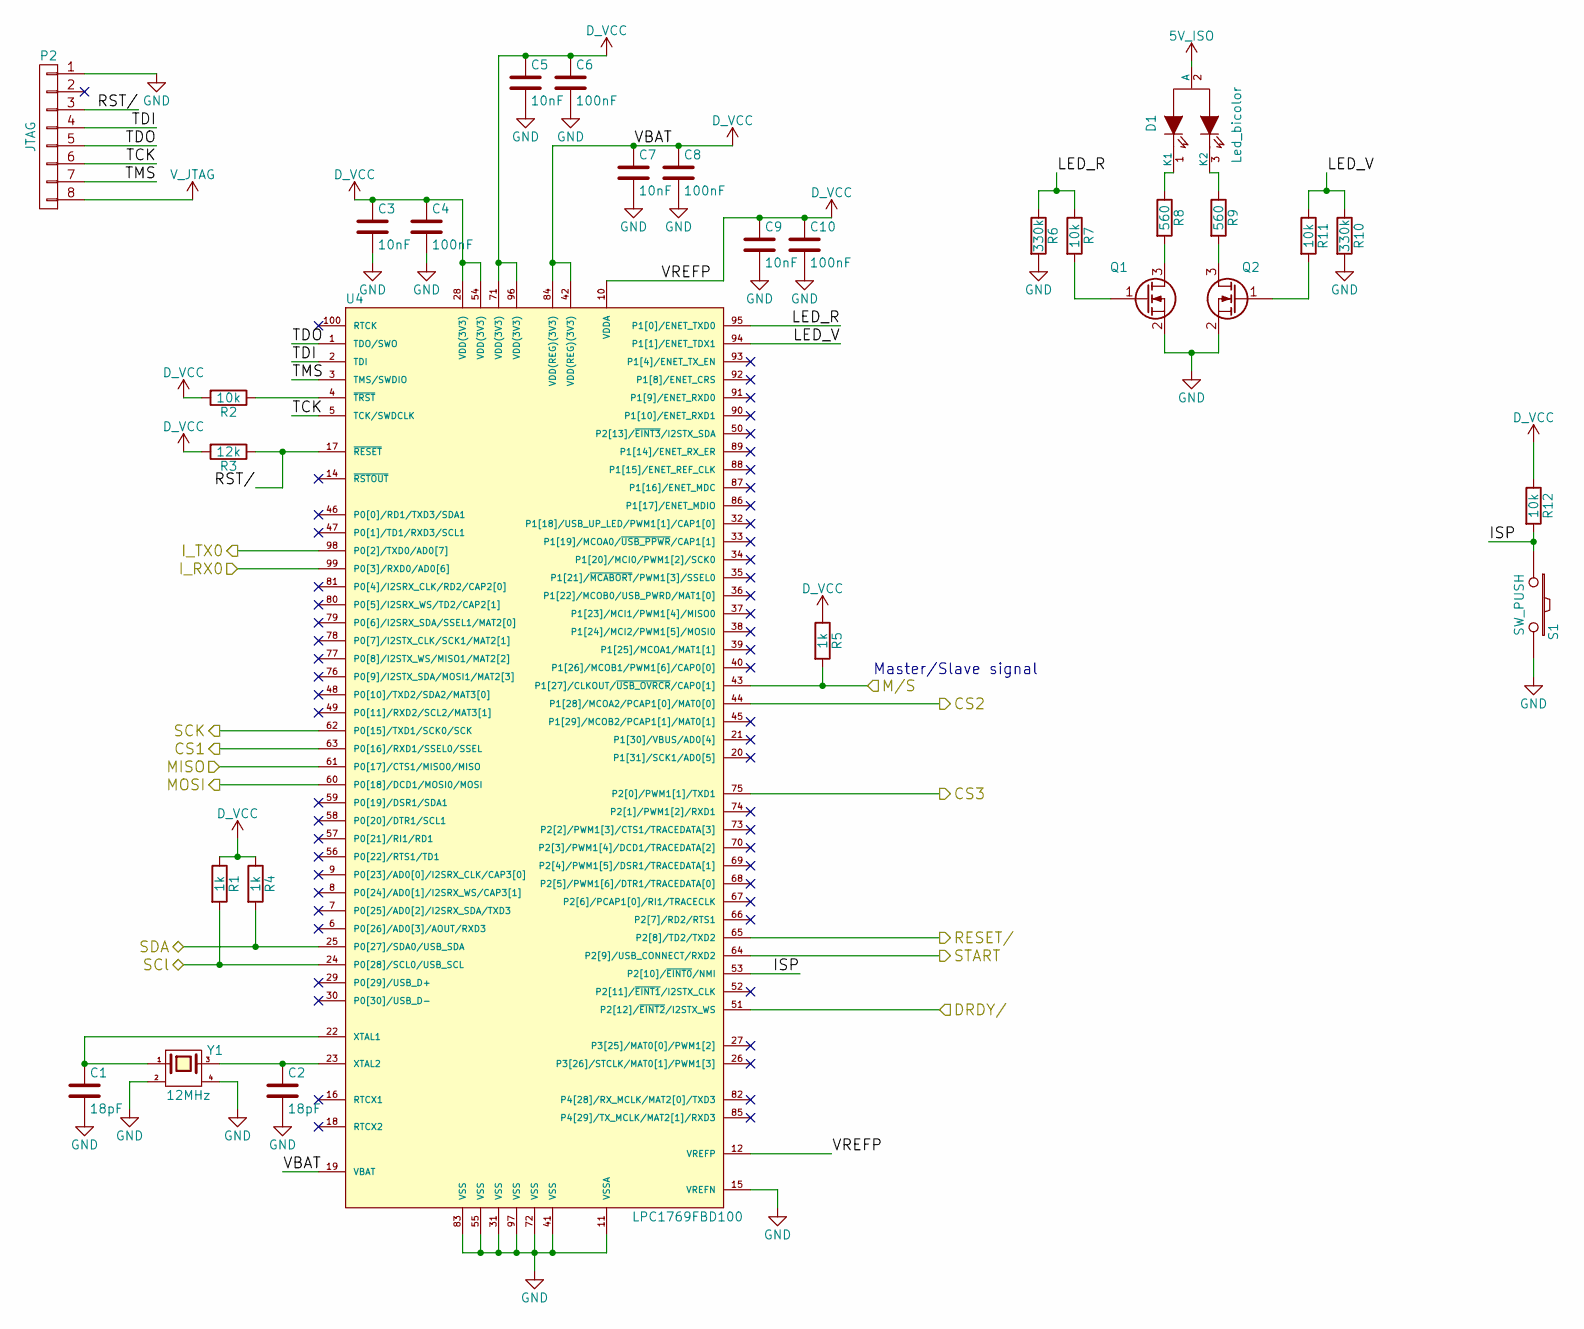
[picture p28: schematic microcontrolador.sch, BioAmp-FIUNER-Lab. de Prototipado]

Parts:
C1, C2: 18pF; C_0603
C3, C5, C7, C9: 10nF; C_0603
C4, C6, C8, C10: 100nF; C_0603
D1: Led_bicolor
P2: JTAG; Pin_Header_Straight_1x08
Q1, Q2: Q_NMOS_SGD-RESCUE-Biopotenciales_LIRINS_v2
R1, R4, R5: 1k; R_0603
R2, R7, R11, R12: 10k; R_0603
R3: 12k; R_0603
R6, R10: 330k; R_0603
R8, R9: 560; R_0603
S1: SW_PUSH; SW_Tactile_SPST_Angled
U4: LPC1769FBD100; LQFP-100_14x14mm_Pitch0.5mm
Y1: 12MHz; XTAL_AM3B

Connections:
5V_ISO: D1.2 (A); also elsewhere on the board
/Analog Front End/DRDY/: U4.51 (P2[12]/~EINT2~/I2STX_WS); also elsewhere on the board
/Analog Front End/M/S: R5.2, U4.43 (P1[27]/CLKOUT/~USB_OVRCR~/CAP0[1]); also elsewhere on the board
/Analog Front End/MISO: U4.61 (P0[17]/CTS1/MISO0/MISO); also elsewhere on the board
/Analog Front End/MOSI: U4.60 (P0[18]/DCD1/MOSI0/MOSI); also elsewhere on the board
/Analog Front End/RESET/: U4.65 (P2[8]/TD2/TXD2); also elsewhere on the board
/Analog Front End/START: U4.64 (P2[9]/USB_CONNECT/RXD2); also elsewhere on the board
/Comunicacion USB/I_RX0: U4.99 (P0[3]/RXD0/AD0[6]); also elsewhere on the board
/Comunicacion USB/I_TX0: U4.98 (P0[2]/TXD0/AD0[7]); also elsewhere on the board
/Interfaz Interconectividad/CS1: U4.63 (P0[16]/RXD1/SSEL0/SSEL); also elsewhere on the board
/Interfaz Interconectividad/CS2: U4.44 (P1[28]/MCOA2/PCAP1[0]/MAT0[0]); also elsewhere on the board
/Interfaz Interconectividad/CS3: U4.75 (P2[0]/PWM1[1]/TXD1); also elsewhere on the board
/Interfaz Interconectividad/SCL: R1.2, U4.24 (P0[28]/SCL0/USB_SCL); also elsewhere on the board
/Interfaz Interconectividad/SDA: R4.2, U4.25 (P0[27]/SDA0/USB_SDA); also elsewhere on the board
/Microcontrolador/ISP: R12.2, S1.1, U4.53 (P2[10]/~EINT0~/NMI)
/Microcontrolador/LED_R: R6.1, R7.1, U4.95 (P1[0]/ENET_TXD0)
/Microcontrolador/LED_V: R10.1, R11.1, U4.94 (P1[1]/ENET_TDX1)
/Microcontrolador/RST/: P2.3, R3.1, U4.17 (~RESET~)
/Microcontrolador/SCK: U4.62 (P0[15]/TXD1/SCK0/SCK); also elsewhere on the board
/Microcontrolador/TCK: P2.6, U4.5 (TCK/SWDCLK)
/Microcontrolador/TDI: P2.4, U4.2 (TDI)
/Microcontrolador/TDO: P2.5, U4.1 (TDO/SWO)
/Microcontrolador/TMS: P2.7, U4.3 (TMS/SWDIO)
D_VCC: C3.1, C4.1, C5.1, C6.1, C7.1, C8.1, C9.1, C10.1, R1.1, R2.2, R3.2, R4.1, R5.1, R12.1, U4.10 (VDDA), U4.12 (VREFP), U4.19 (VBAT), U4.28 (VDD(3V3)), U4.42 (VDD(REG)(3V3)), U4.54 (VDD(3V3)), U4.71 (VDD(3V3)), U4.84 (VDD(REG)(3V3)), U4.96 (VDD(3V3)); also elsewhere on the board
GND: C1.2, C2.2, C3.2, C4.2, C5.2, C6.2, C7.2, C8.2, C9.2, C10.2, P2.1, Q1.2 (S), Q2.2 (S), R6.2, R10.2, S1.2, U4.11 (VSSA), U4.15 (VREFN), U4.31 (VSS), U4.41 (VSS), U4.55 (VSS), U4.72 (VSS), U4.83 (VSS), U4.97 (VSS), Y1.2, Y1.4; also elsewhere on the board
unnamed: C1.1, U4.22 (XTAL1), Y1.1
unnamed: C2.1, U4.23 (XTAL2), Y1.3 (case)
unnamed: D1.1 (K1), R8.1
unnamed: D1.3 (K2), R9.1
unnamed: Q1.1 (G), R7.2
unnamed: Q1.3 (D), R8.2
unnamed: Q2.1 (G), R11.2
unnamed: Q2.3 (D), R9.2
unnamed: R2.1, U4.4 (~TRST~)
V_JATG: P2.8

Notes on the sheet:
Master/Slave signal

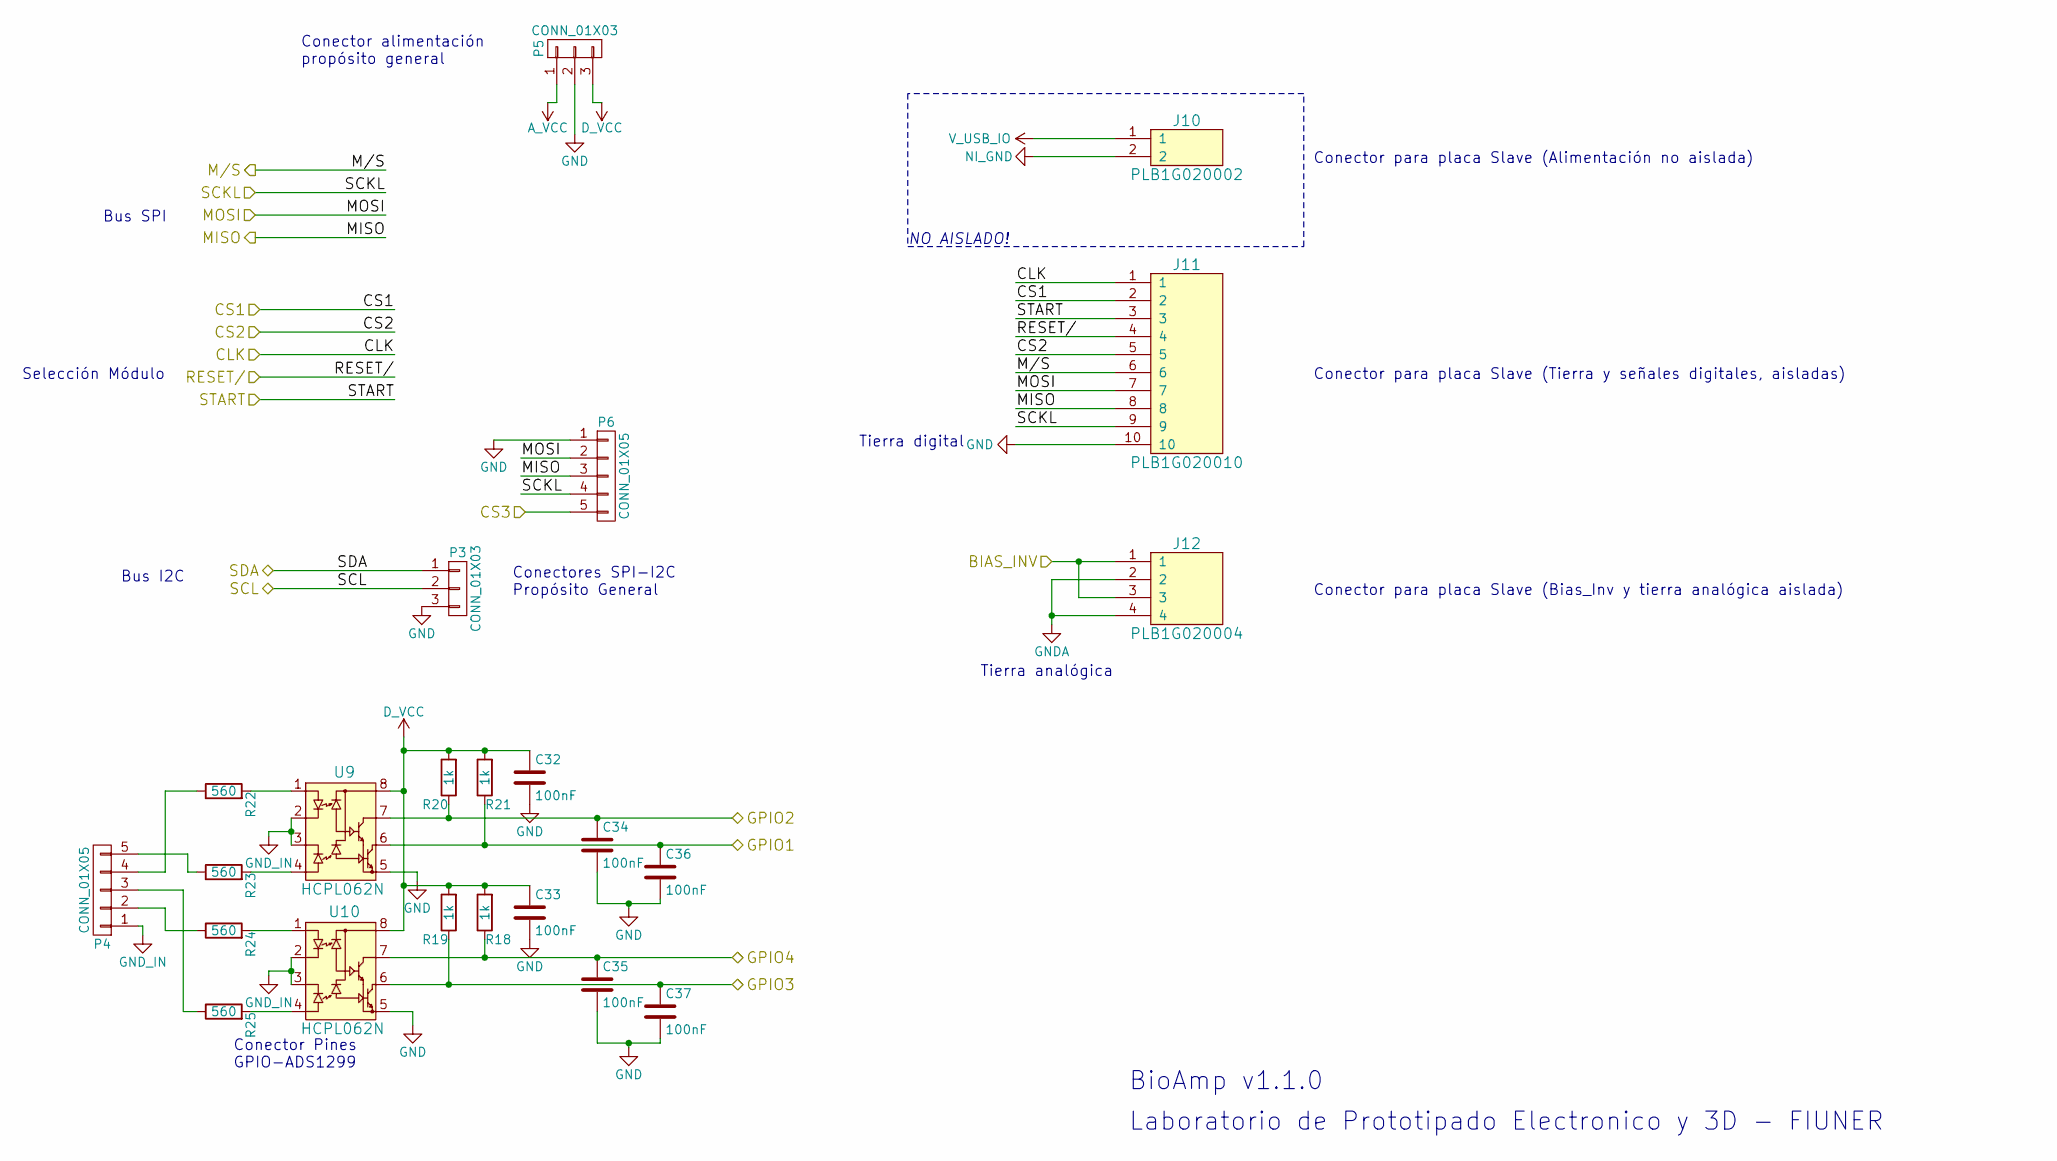
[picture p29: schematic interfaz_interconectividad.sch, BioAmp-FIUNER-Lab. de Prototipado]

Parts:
C32, C33, C34, C35, C36, C37: 100nF; C_0603
J10: PLB1G020002
J11: PLB1G020010
J12: PLB1G020004
P3, P5: CONN_01X03; Pin_Header_Straight_1x03
P4, P6: CONN_01X05; Pin_Header_Straight_1x05
R18, R19, R20, R21: 1k; R_0603
R22, R23, R24, R25: 560; R_0603
U9, U10: HCPL062N; SOIC-8_3.9x4.9mm_Pitch1.27mm

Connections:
/Analog Front End/BIAS_INV: J12.1, J12.3; also elsewhere on the board
/Analog Front End/CLK: J11.1; also elsewhere on the board
/Analog Front End/GPIO1: C36.1, R21.1, U9.6; also elsewhere on the board
/Analog Front End/GPIO2: C34.1, R20.1, U9.7; also elsewhere on the board
/Analog Front End/GPIO3: C37.1, R19.1, U10.6; also elsewhere on the board
/Analog Front End/GPIO4: C35.1, R18.1, U10.7; also elsewhere on the board
/Analog Front End/M/S: J11.6; also elsewhere on the board
/Analog Front End/MISO: J11.8, P6.3; also elsewhere on the board
/Analog Front End/MOSI: J11.7, P6.2; also elsewhere on the board
/Analog Front End/RESET/: J11.4; also elsewhere on the board
/Analog Front End/START: J11.3; also elsewhere on the board
/Interfaz Interconectividad/CS1: J11.2; also elsewhere on the board
/Interfaz Interconectividad/CS2: J11.5; also elsewhere on the board
/Interfaz Interconectividad/CS3: P6.5; also elsewhere on the board
/Interfaz Interconectividad/SCL: P3.2; also elsewhere on the board
/Interfaz Interconectividad/SDA: P3.1; also elsewhere on the board
/Microcontrolador/SCK: J11.9, P6.4; also elsewhere on the board
A_VCC: P5.1; also elsewhere on the board
D_VCC: C32.1, C33.1, P5.3, R18.2, R19.2, R20.2, R21.2, U9.8, U10.8; also elsewhere on the board
GND: C32.2, C33.2, C34.2, C35.2, C36.2, C37.2, J11.10, P3.3, P5.2, P6.1, U9.5, U10.5; also elsewhere on the board
GNDA: J12.2, J12.4; also elsewhere on the board
GND_IN: P4.1, U9.2, U9.3, U10.2, U10.3
NI_GND: J10.2; also elsewhere on the board
unnamed: P4.2, R24.1
unnamed: P4.3, R25.1
unnamed: P4.4, R22.1
unnamed: P4.5, R23.1
unnamed: R22.2, U9.1
unnamed: R23.2, U9.4
unnamed: R24.2, U10.1
unnamed: R25.2, U10.4
V_USB_IO: J10.1; also elsewhere on the board

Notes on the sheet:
Conector alimentación propósito general
Bus SPI
Selección Módulo
Bus I2C
Conector Pines GPIO-ADS1299
Conectores SPI-I2C Propósito General
Tierra analógica
Conector para placa Slave (Bias_Inv y tierra analógica aislada)
Conector para placa Slave (Tierra y señales digitales, aisladas)
Conector para placa Slave (Alimentación no aislada)
NO AISLADO!
Tierra digital
BioAmp v1.1.0
Laboratorio de Prototipado Electronico y 3D - FIUNER

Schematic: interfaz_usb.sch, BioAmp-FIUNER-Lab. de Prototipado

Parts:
C11, C16: 0.1uF; C_0603
C12, C17, C19: 10uF; C_0603
C13: 10nF; C_0603
C14, C15: 47pF; C_0603
C18, C22: 100nF; C_0603
C20: 4.7uF; c_tant_A
C21, C23: 1uF; C_0603
D2: D_Schottky; diode_0603
D4: LED; LED_0603
J13: USB_B; USB_B-smd
L1, L2, L3, L4: INDUCTOR_SMALL; FER-0805
NT1: Net_Tie; Net_tie
R13, R14: 27; R_0603
R15: 0R; R_0603
R16: 560; R_0603
U5: ADUM6201CRWZ; SOIC-16_7.5x10.3mm_Pitch1.27mm
U6: TPD2E001DRLR; 5-Flat_Leads_1.2x1.6mmPitch_0.5mm
U7: FT230XS; SSOP-16_3.9x4.9mm_Pitch0.635mm
VR1: LP5907_3.3V; sot23-5

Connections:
5V_ISO: C16.1, C17.1, C19.1, C21.1, L3.1, U5.10 (VE2), U5.11 (VSEL), U5.16 (VISO), VR1.1 (IN), VR1.3 (EN); also elsewhere on the board
5V_NI: C11.1, C12.1, D2.C, L4.1, U5.1 (VDD1), U5.6 (RCSEL), U5.7 (VE1)
/Comunicacion USB/3V3OUT: C22.1, U7.3 (VCCIO), U7.10 (3V3OUT), U7.11 (~RESET)
/Comunicacion USB/D_N: C14.1, J13.2 (D-), R13.2, U6.3 (IO1)
/Comunicacion USB/D_P: C15.1, J13.3 (D+), R14.2, U6.5 (IO2)
/Comunicacion USB/I_RX0: U5.14 (VOA); also elsewhere on the board
/Comunicacion USB/I_TX0: U5.13 (VIB); also elsewhere on the board
/Comunicacion USB/RX0: U5.3 (VIA), U7.1 (TXD)
/Comunicacion USB/TX0: U5.4 (VOA), U7.4 (RXD)
/Comunicacion USB/USBD+: R14.1, U7.8 (USBDP)
/Comunicacion USB/USBD-: R13.1, U7.9 (USBDM)
A_VCC: L3.2; also elsewhere on the board
D_VCC: C23.1, VR1.5 (OUT); also elsewhere on the board
GND: C23.2, NT1.2; also elsewhere on the board
GNDA: C16.2, C17.2, C19.2, C21.2, NT1.1, U5.9 (GNDISO), U5.15 (GNDISO), VR1.2 (GND); also elsewhere on the board
NI_GND: C11.2, C12.2, C13.2, C14.2, C15.2, C18.2, C20.2, C22.2, J13.4 (GND), L1.2, U5.2 (GND1), U5.5 (RCIN), U5.8 (GND1), U6.4 (GND), U7.5 (GND), U7.13 (GND); also elsewhere on the board
unnamed: C13.1, J13.1 (VCC), L2.2
unnamed: D4.1 (K), R16.1
unnamed: J13.5 (shield), L1.1
unnamed: R15.1, U7.2 (~RTS)
unnamed: R15.2, U7.6 (~CTS)
unnamed: R16.2, U7.14 (CBUS1)
V_USB: C18.1, C20.1, D2.A, D4.2 (A), L2.1, U6.1 (VCC), U7.12 (VCC)
V_USB_IO: L4.2; also elsewhere on the board

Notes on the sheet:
NO AISLADO!
NO AISLADO!
NO AISLADO!
Filtrado alimentación analógica
I/O alimentación No-Aislada

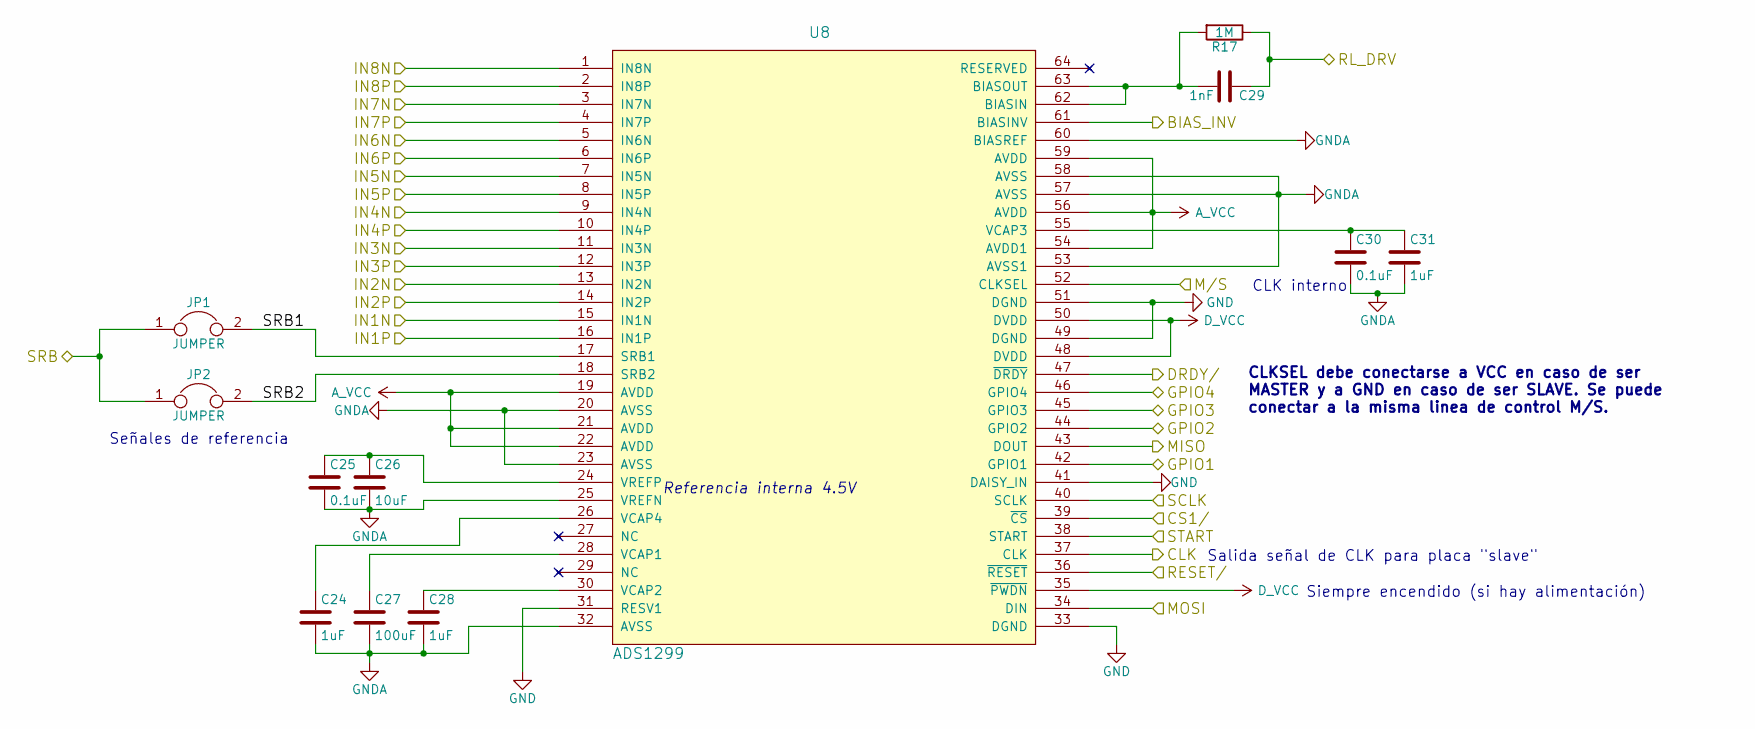
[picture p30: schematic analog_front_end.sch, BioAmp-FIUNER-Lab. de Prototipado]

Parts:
C24, C28, C31: 1uF; C_0603
C25, C30: 0.1uF; C_0603
C26: 10uF; C_0603
C27: 100uF; C_1206
C29: 1nF; C_0603
JP1, JP2: JUMPER; R_0603
R17: 1M; R_0603
U8: ADS1299; LQFP-64_10x10mm_Pitch0.5mm

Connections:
/Analog Front End/BIAS_INV: U8.61 (BIASINV); also elsewhere on the board
/Analog Front End/CLK: U8.37 (CLK); also elsewhere on the board
/Analog Front End/DRDY/: U8.47 (~DRDY~); also elsewhere on the board
/Analog Front End/GPIO1: U8.42 (GPIO1); also elsewhere on the board
/Analog Front End/GPIO2: U8.44 (GPIO2); also elsewhere on the board
/Analog Front End/GPIO3: U8.45 (GPIO3); also elsewhere on the board
/Analog Front End/GPIO4: U8.46 (GPIO4); also elsewhere on the board
/Analog Front End/M/S: U8.52 (CLKSEL); also elsewhere on the board
/Analog Front End/MISO: U8.43 (DOUT); also elsewhere on the board
/Analog Front End/MOSI: U8.34 (DIN); also elsewhere on the board
/Analog Front End/RESET/: U8.36 (~RESET~); also elsewhere on the board
/Analog Front End/RL_DRV: C29.1, R17.1; also elsewhere on the board
/Analog Front End/SRB1: JP1.2, U8.17 (SRB1); also elsewhere on the board
/Analog Front End/SRB2: JP2.2, U8.18 (SRB2); also elsewhere on the board
/Analog Front End/START: U8.38 (START); also elsewhere on the board
/Entradas Analogicas/IN1+: U8.16 (IN1P); also elsewhere on the board
/Entradas Analogicas/IN1-: U8.15 (IN1N); also elsewhere on the board
/Entradas Analogicas/IN2+: U8.14 (IN2P); also elsewhere on the board
/Entradas Analogicas/IN2-: U8.13 (IN2N); also elsewhere on the board
/Entradas Analogicas/IN3+: U8.12 (IN3P); also elsewhere on the board
/Entradas Analogicas/IN3-: U8.11 (IN3N); also elsewhere on the board
/Entradas Analogicas/IN4+: U8.10 (IN4P); also elsewhere on the board
/Entradas Analogicas/IN4-: U8.9 (IN4N); also elsewhere on the board
/Entradas Analogicas/IN5+: U8.8 (IN5P); also elsewhere on the board
/Entradas Analogicas/IN5-: U8.7 (IN5N); also elsewhere on the board
/Entradas Analogicas/IN6+: U8.6 (IN6P); also elsewhere on the board
/Entradas Analogicas/IN6-: U8.5 (IN6N); also elsewhere on the board
/Entradas Analogicas/IN7+: U8.4 (IN7P); also elsewhere on the board
/Entradas Analogicas/IN7-: U8.3 (IN7N); also elsewhere on the board
/Entradas Analogicas/IN8+: U8.2 (IN8P); also elsewhere on the board
/Entradas Analogicas/IN8-: U8.1 (IN8N); also elsewhere on the board
/Interfaz Interconectividad/CS1: U8.39 (~CS~); also elsewhere on the board
/Microcontrolador/SCK: U8.40 (SCLK); also elsewhere on the board
A_VCC: U8.19 (AVDD), U8.21 (AVDD), U8.22 (AVDD), U8.54 (AVDD1), U8.56 (AVDD), U8.59 (AVDD); also elsewhere on the board
D_VCC: U8.35 (~PWDN~), U8.48 (DVDD), U8.50 (DVDD); also elsewhere on the board
GND: U8.31 (RESV1), U8.33 (DGND), U8.41 (DAISY_IN), U8.49 (DGND), U8.51 (DGND); also elsewhere on the board
GNDA: C24.2, C25.2, C26.2, C27.2, C28.2, C30.2, C31.2, U8.20 (AVSS), U8.23 (AVSS), U8.25 (VREFN), U8.32 (AVSS), U8.53 (AVSS1), U8.57 (AVSS), U8.58 (AVSS), U8.60 (BIASREF); also elsewhere on the board
unnamed: C24.1, U8.26 (VCAP4)
unnamed: C25.1, C26.1, U8.24 (VREFP)
unnamed: C27.1, U8.28 (VCAP1)
unnamed: C28.1, U8.30 (VCAP2)
unnamed: C29.2, R17.2, U8.62 (BIASIN), U8.63 (BIASOUT)
unnamed: C30.1, C31.1, U8.55 (VCAP3)
unnamed: JP1.1, JP2.1

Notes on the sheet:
CLK interno
Salida señal de CLK para placa "slave"
Señales de referencia
Siempre encendido (si hay alimentación)
Referencia interna 4.5V
CLKSEL debe conectarse a VCC en caso de ser MASTER y a GND en caso de ser SLAVE. Se puede conectar a la misma linea de control M/S.

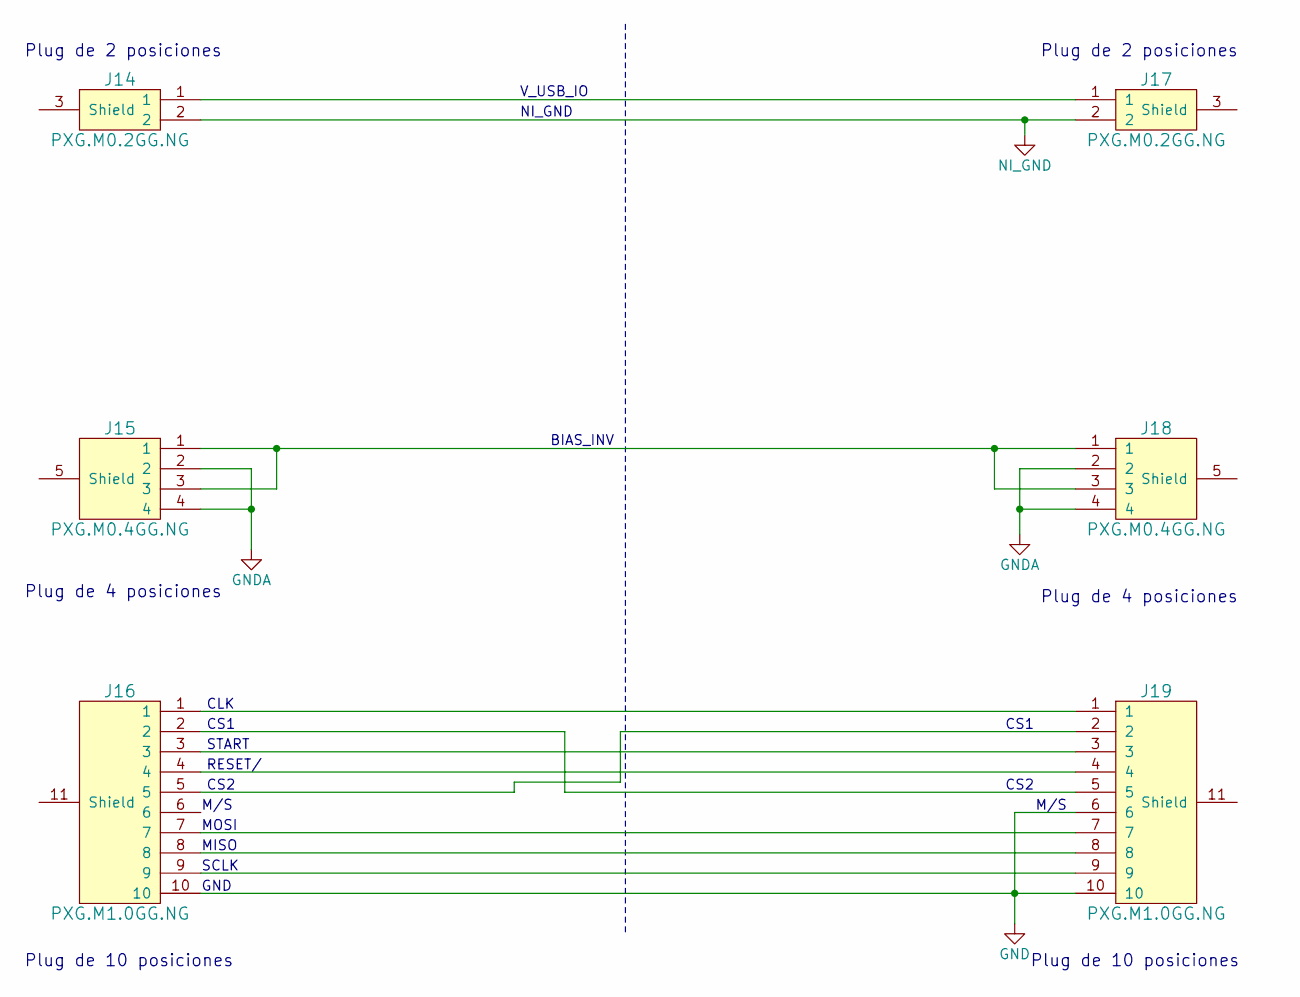
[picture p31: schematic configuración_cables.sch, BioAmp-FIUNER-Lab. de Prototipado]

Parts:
J14, J17: PXG.M0.2GG.NG
J15, J18: PXG.M0.4GG.NG
J16, J19: PXG.M1.0GG.NG

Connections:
unnamed: J14.1, J17.1
unnamed: J14.2, J17.2
unnamed: J15.1, J15.3, J18.1, J18.3
unnamed: J15.2, J15.4, J18.2, J18.4
unnamed: J16.1, J19.1
unnamed: J16.2, J19.5
unnamed: J16.3, J19.3
unnamed: J16.4, J19.4
unnamed: J16.5, J19.2
unnamed: J16.7, J19.7
unnamed: J16.8, J19.8
unnamed: J16.9, J19.9
unnamed: J16.10, J19.6, J19.10

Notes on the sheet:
Plug de 2 posiciones
Plug de 4 posiciones
Plug de 10 posiciones
CLK
CS1
START
RESET/
CS2
M/S
MOSI
MISO
SCLK
GND
CS1
BIAS_INV
V_USB_IO
NI_GND

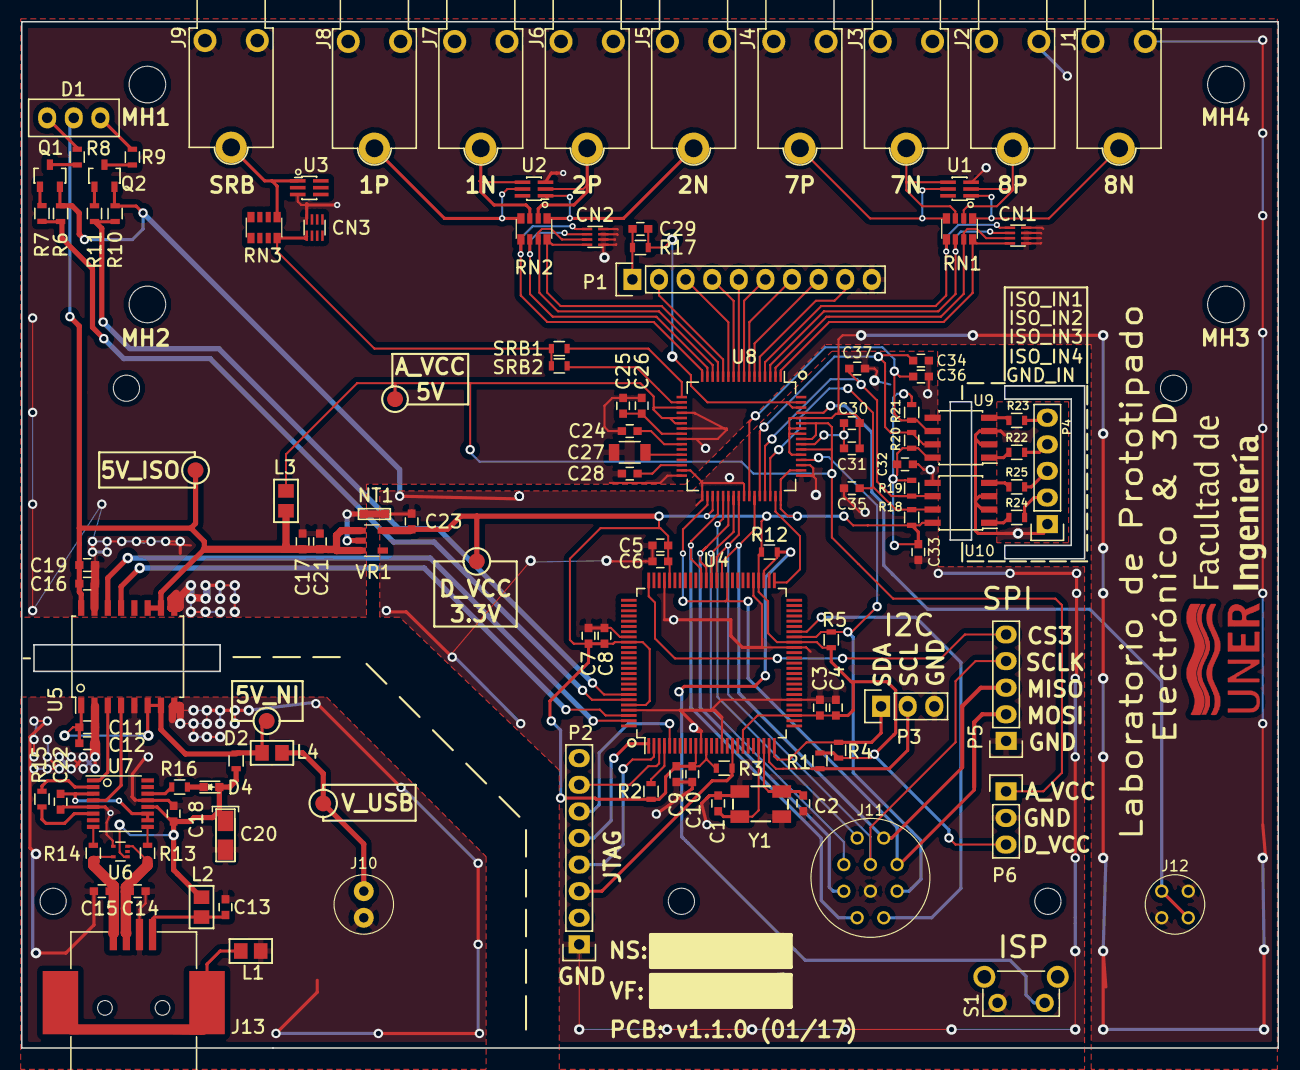
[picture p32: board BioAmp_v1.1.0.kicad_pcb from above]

Board: 2 copper layers, 120.0 x 98.0 mm, 116 parts (0 on the bottom side), 103 nets.

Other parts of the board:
MH1, MH2, MH3, MH4: MountingHole_3-5mm
SRB1, SRB2: JUMPER; R_0603

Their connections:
/Analog Front End/SRB1: SRB1.2; also elsewhere on the board
/Analog Front End/SRB2: SRB2.2; also elsewhere on the board
/Entradas Analogicas/IN_SRB: SRB1.1, SRB2.1; also elsewhere on the board

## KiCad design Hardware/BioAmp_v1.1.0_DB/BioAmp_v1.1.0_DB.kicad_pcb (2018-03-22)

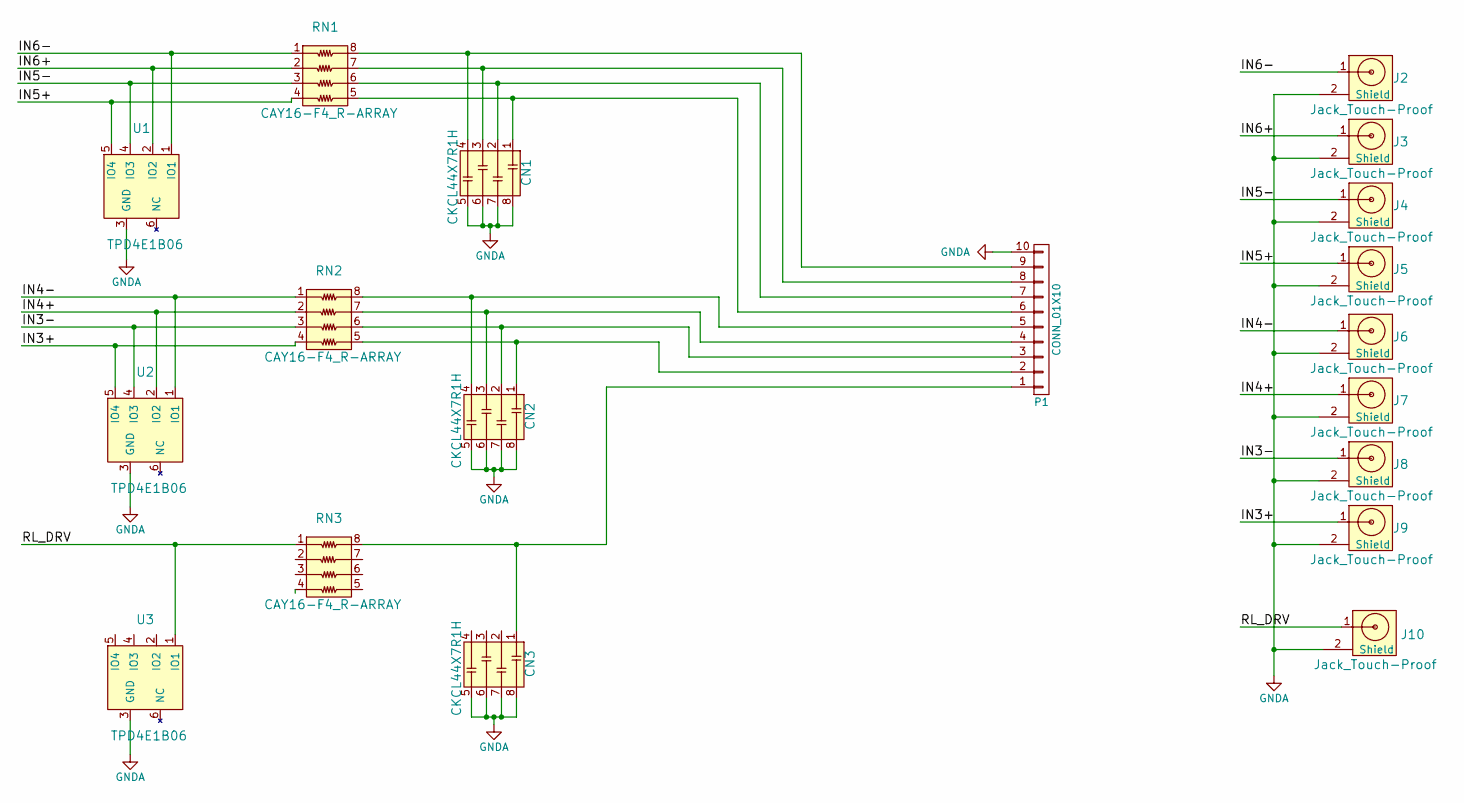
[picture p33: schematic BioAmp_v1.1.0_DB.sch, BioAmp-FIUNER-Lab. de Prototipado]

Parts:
CN1, CN2, CN3: CKCL44X7R1H; Cap_Array_4
J2, J3, J4, J6, J7, J8, J9: Jack_Touch-Proof; Jack_TouchProof_1.5mm
J5, J10: Jack_Touch-Proof
P1: CONN_01X10; Pin_Header_Straight_1x10
RN1, RN2, RN3: CAY16-F4_R-ARRAY; r_cay16-4
U1, U2, U3: TPD4E1B06; TSOP-6_2x1.25mm_Pitch0.65mm

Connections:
/IN3+: J9.1, RN2.4, U2.5 (IO4)
/IN3-: J8.1, RN2.3, U2.4 (IO3)
/IN4+: J7.1, RN2.2, U2.2 (IO2)
/IN4-: J6.1, RN2.1, U2.1 (IO1)
/IN5+: J5.1, RN1.4, U1.5 (IO4)
/IN5-: J4.1, RN1.3, U1.4 (IO3)
/IN6+: J3.1, RN1.2, U1.2 (IO2)
/IN6-: J2.1, RN1.1, U1.1 (IO1)
/RL_DRV: J10.1, RN3.1, U3.1 (IO1)
GNDA: CN1.5, CN1.6, CN1.7, CN1.8, CN2.5, CN2.6, CN2.7, CN2.8, CN3.5, CN3.6, CN3.7, CN3.8, J2.2 (Shield), J3.2 (Shield), J4.2 (Shield), J5.2 (Shield), J6.2 (Shield), J7.2 (Shield), J8.2 (Shield), J9.2 (Shield), J10.2 (Shield), P1.10, U1.3 (GND), U2.3 (GND), U3.3 (GND)
unnamed: CN1.1, P1.6, RN1.5
unnamed: CN1.2, P1.7, RN1.6
unnamed: CN1.3, P1.8, RN1.7
unnamed: CN1.4, P1.9, RN1.8
unnamed: CN2.1, P1.2, RN2.5
unnamed: CN2.2, P1.3, RN2.6
unnamed: CN2.3, P1.4, RN2.7
unnamed: CN2.4, P1.5, RN2.8
unnamed: CN3.1, P1.1, RN3.8

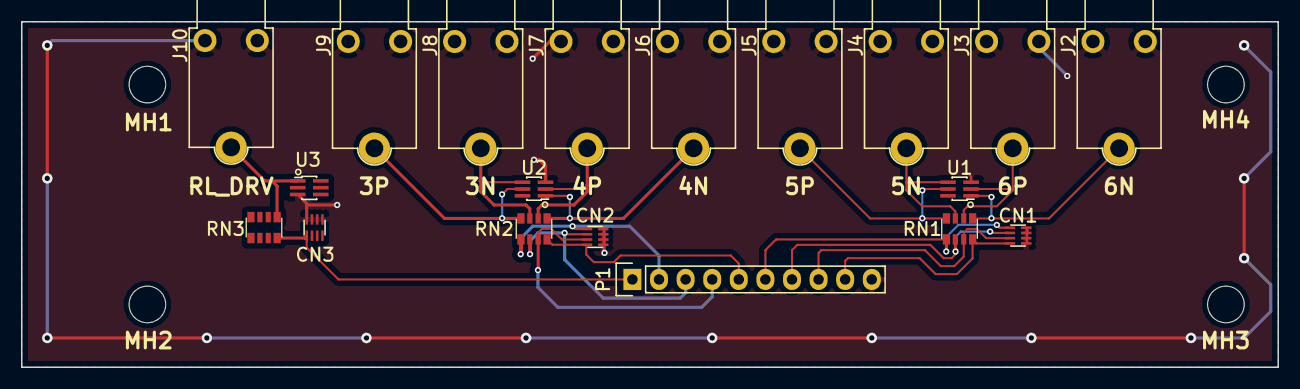
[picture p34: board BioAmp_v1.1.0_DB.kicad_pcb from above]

Board: 2 copper layers, 120.0 x 33.0 mm, 23 parts (0 on the bottom side), 19 nets.

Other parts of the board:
MH1, MH2, MH3, MH4: MountingHole_3-5mm

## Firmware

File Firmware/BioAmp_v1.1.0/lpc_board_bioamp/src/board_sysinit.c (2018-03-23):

/*
 * @brief BioAmp -Sysinit file
 *
 * @note
 * Copyright(C) NXP Semiconductors, 2013
 * All rights reserved.
 *
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
 * @par
 * Permission to use, copy, modify, and distribute this software and its
 * documentation is hereby granted, under NXP Semiconductors' and its
 * licensor's relevant copyrights in the software, without fee, provided that it
 * is used in conjunction with NXP Semiconductors microcontrollers.  This
 * copyright, permission, and disclaimer notice must appear in all copies of
 * this code.
 */

#include "board_api.h"
#include "chip.h"

/* The System initialization code is called prior to the application and
   initializes the board for run-time operation. Board initialization
   includes clock setup and default pin muxing configuration. */

/*****************************************************************************
 * Private types/enumerations/variables
 ****************************************************************************/


//TODO: BioAmp project pin muxing
STATIC const PINMUX_GRP_T pinmuxing[] = {
		{1, 27, IOCON_MODE_INACT | IOCON_FUNC0},	// M/S signal (GPIO funcionality)
		{0, 16, IOCON_MODE_INACT | IOCON_FUNC0},	// CS1 signal (GPIO funcionality)
		{1, 28, IOCON_MODE_INACT | IOCON_FUNC0},	// CS2 signal (GPIO funcionality)
		{2, 8, IOCON_MODE_INACT | IOCON_FUNC0},		// RESET/ signal (GPIO funcionality)
	//	{2, 8, IOCON_MODE_PULLUP | IOCON_FUNC0},
		{2, 9, IOCON_MODE_INACT | IOCON_FUNC0},		// START signal (GPIO funcionality)
		{2, 12, IOCON_MODE_INACT | IOCON_FUNC0},	// DRDY/ signal (GPIO funcionality)
		{2, 10, IOCON_MODE_INACT | IOCON_FUNC0},	// ISP signal (GPIO funcionality)
		{1, 0, IOCON_MODE_INACT | IOCON_FUNC0},		// LED_R signal (GPIO funcionality)
		{1, 1, IOCON_MODE_INACT | IOCON_FUNC0},		// LED_V signal (GPIO funcionality)
		{0, 15, IOCON_MODE_INACT | IOCON_FUNC2},	// SSP SCK signal (SCK0 funcionality)
		{0, 17, IOCON_MODE_INACT | IOCON_FUNC2},	// SSP MISO signal (MISO0 funcionality)
		{0, 18, IOCON_MODE_INACT | IOCON_FUNC2},	// SSP MOSI signal (MOSI0 funcionality)
		{0, 2, IOCON_MODE_INACT | IOCON_FUNC1},		// UART TX signal (TXD0 funcionality)
		{0, 3, IOCON_MODE_INACT | IOCON_FUNC1},		// UART RX signal (RXD0 funcionality)

		/* SSP1 pin muxing */
		{0, 7, IOCON_MODE_INACT | IOCON_FUNC2},
		{0, 6, IOCON_MODE_INACT | IOCON_FUNC2},
		{0, 8, IOCON_MODE_INACT | IOCON_FUNC2},
		{0, 9, IOCON_MODE_INACT | IOCON_FUNC2},

		/*Additional Configurations supported by the "Biopotenciales-LIRINS" board */

		//{2, 0, IOCON_MODE_INACT | IOCON_FUNC0},		// CS3 signal (GPIO funcionality)
		//{0, 27, IOCON_MODE_INACT | IOCON_FUNC1},		// I2C SDA signal (SDA0 funcionality)
		//{0, 28, IOCON_MODE_INACT | IOCON_FUNC1},		// I2C SCL signal (SCL0 funcionality)

		/* Configurations for LPC1769 Stick  */
		//{0,  0,   IOCON_MODE_INACT | IOCON_FUNC2},	/* TXD3 */
		//{0,  1,   IOCON_MODE_INACT | IOCON_FUNC2},	/* RXD3 */
		//{0,  22,  IOCON_MODE_INACT | IOCON_FUNC0},	/* Led 0 */
		//{0x1, 27, IOCON_MODE_INACT | IOCON_FUNC1},	/* CLKOUT */

};

/*****************************************************************************
 * Public types/enumerations/variables
 ****************************************************************************/
/* System oscillator rate and RTC oscillator rate */
const uint32_t OscRateIn = 12000000;

//TODO: not use RTC
const uint32_t RTCOscRateIn = 0;

/*****************************************************************************
 * Private functions
 ****************************************************************************/

/*****************************************************************************
 * Public functions
 ****************************************************************************/

/* Sets up system pin muxing */
void Board_SetupMuxing(void)
{
	Chip_IOCON_SetPinMuxing(LPC_IOCON, pinmuxing, sizeof(pinmuxing) / sizeof(PINMUX_GRP_T));
}

/* Setup system clocking */
void Board_SetupClocking(void)
{
	Chip_SetupXtalClocking();

	/* Setup FLASH access to 4 clocks (100MHz clock) */
	Chip_SYSCTL_SetFLASHAccess(FLASHTIM_100MHZ_CPU);

	/* Enable and setup SysTick Timer at a periodic rate */
//	SysTick_Config(SystemCoreClock / TICKRATE_HZ1);
}

/* Set up and initialize hardware prior to call to main */
void Board_SystemInit(void)
{
	Board_SetupMuxing();
	Board_SetupClocking();
}

/* Set up and initialize all required blocks and functions related to the
   board hardware */
void Board_Init(void)
{
	Chip_IOCON_Init(LPC_IOCON);

}

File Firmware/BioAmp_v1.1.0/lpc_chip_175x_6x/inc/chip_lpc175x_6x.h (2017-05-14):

/*
 * @brief LPC175x/6x basic chip inclusion file
 *
 * @note
 * Copyright(C) NXP Semiconductors, 2014
 * All rights reserved.
 *
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
 * @par
 * Permission to use, copy, modify, and distribute this software and its
 * documentation is hereby granted, under NXP Semiconductors' and its
 * licensor's relevant copyrights in the software, without fee, provided that it
 * is used in conjunction with NXP Semiconductors microcontrollers.  This
 * copyright, permission, and disclaimer notice must appear in all copies of
 * this code.
 */

#ifndef __CHIP_LPC175X_6X_H_
#define __CHIP_LPC175X_6X_H_

#include "lpc_types.h"
#include "sys_config.h"
#include "cmsis.h"

#ifdef __cplusplus
extern "C" {
#endif

#if !defined(CORE_M3)
#error CORE_M3 is not defined for the LPC175x/6x architecture
#error CORE_M3 should be defined as part of your compiler define list
#endif

#ifndef CHIP_LPC175X_6X
#error CHIP_LPC175X_6X is not defined!
#endif

/** @defgroup PERIPH_175X_6X_BASE CHIP: LPC175x/6x Peripheral addresses and register set declarations
 * @ingroup CHIP_17XX_40XX_Drivers
 * @{
 */

#define LPC_GPIO0_BASE            0x2009C000
#define LPC_GPIO1_BASE            0x2009C020
#define LPC_GPIO2_BASE            0x2009C040
#define LPC_GPIO3_BASE            0x2009C060
#define LPC_GPIO4_BASE            0x2009C080

/* APB0 peripheral */
#define LPC_WWDT_BASE             0x40000000
#define LPC_TIMER0_BASE           0x40004000
#define LPC_TIMER1_BASE           0x40008000
#define LPC_UART0_BASE            0x4000C000
#define LPC_UART1_BASE            0x40010000
#define LPC_PWM1_BASE             0x40018000
#define LPC_I2C0_BASE             0x4001C000
#define LPC_SPI_BASE              0x40020000
#define LPC_RTC_BASE              0x40024000
#define LPC_REGFILE_BASE          0x40024044
#define LPC_GPIOINT_BASE          0x40028080
#define LPC_IOCON_BASE            0x4002C000
#define LPC_SSP1_BASE             0x40030000
#define LPC_ADC_BASE              0x40034000
#define LPC_CANAF_RAM_BASE        0x40038000
#define LPC_CANAF_BASE            0x4003C000
#define LPC_CANCR_BASE            0x40040000
#define LPC_CAN1_BASE             0x40044000
#define LPC_CAN2_BASE             0x40048000
#define LPC_I2C1_BASE             0x4005C000

/* APB1 peripheral */
#define LPC_FMC_BASE              0x40084000
#define LPC_SSP0_BASE             0x40088000
#define LPC_DAC_BASE              0x4008C000
#define LPC_TIMER2_BASE           0x40090000
#define LPC_TIMER3_BASE           0x40094000
#define LPC_UART2_BASE            0x40098000
#define LPC_UART3_BASE            0x4009C000
#define LPC_I2C2_BASE             0x400A0000
#define LPC_I2S_BASE              0x400A8000
#define LPC_RITIMER_BASE          0x400B0000
#define LPC_MCPWM_BASE            0x400B8000
#define LPC_QEI_BASE              0x400BC000
#define LPC_SYSCTL_BASE           0x400FC000
#define LPC_PMU_BASE              0x400FC0C0

/* AHB peripheral */
#define LPC_ENET_BASE             0x50000000
#define LPC_GPDMA_BASE            0x50004000
#define LPC_USB_BASE              0x5000C000

/* Assign LPC_* names to structures mapped to addresses */
#define LPC_PMU                   ((LPC_PMU_T              *) LPC_PMU_BASE)
#define LPC_GPDMA                 ((LPC_GPDMA_T            *) LPC_GPDMA_BASE)
#define LPC_USB                   ((LPC_USB_T              *) LPC_USB_BASE)
#define LPC_ETHERNET              ((LPC_ENET_T             *) LPC_ENET_BASE)
#define LPC_GPIO                  ((LPC_GPIO_T             *) LPC_GPIO0_BASE)
#define LPC_GPIO1                 ((LPC_GPIO_T             *) LPC_GPIO1_BASE)
#define LPC_GPIO2                 ((LPC_GPIO_T             *) LPC_GPIO2_BASE)
#define LPC_GPIO3                 ((LPC_GPIO_T             *) LPC_GPIO3_BASE)
#define LPC_GPIO4                 ((LPC_GPIO_T             *) LPC_GPIO4_BASE)
#define LPC_GPIOINT               ((LPC_GPIOINT_T          *) LPC_GPIOINT_BASE)
#define LPC_RTC                   ((LPC_RTC_T              *) LPC_RTC_BASE)
#define LPC_REGFILE               ((LPC_REGFILE_T          *) LPC_REGFILE_BASE)
#define LPC_WWDT                  ((LPC_WWDT_T             *) LPC_WWDT_BASE)
#define LPC_UART0                 ((LPC_USART_T            *) LPC_UART0_BASE)
#define LPC_UART1                 ((LPC_USART_T            *) LPC_UART1_BASE)
#define LPC_UART2                 ((LPC_USART_T            *) LPC_UART2_BASE)
#define LPC_UART3                 ((LPC_USART_T            *) LPC_UART3_BASE)
#define LPC_SPI                   ((LPC_SPI_T              *) LPC_SPI_BASE)
#define LPC_SSP0                  ((LPC_SSP_T              *) LPC_SSP0_BASE)
#define LPC_SSP1                  ((LPC_SSP_T              *) LPC_SSP1_BASE)
#define LPC_TIMER0                ((LPC_TIMER_T            *) LPC_TIMER0_BASE)
#define LPC_TIMER1                ((LPC_TIMER_T            *) LPC_TIMER1_BASE)
#define LPC_TIMER2                ((LPC_TIMER_T            *) LPC_TIMER2_BASE)
#define LPC_TIMER3                ((LPC_TIMER_T            *) LPC_TIMER3_BASE)
#define LPC_MCPWM                 ((LPC_MCPWM_T            *) LPC_MCPWM_BASE)
#define LPC_PWM1                  ((LPC_PWM_T              *) LPC_PWM1_BASE)
#define LPC_I2C0                  ((LPC_I2C_T              *) LPC_I2C0_BASE)
#define LPC_I2C1                  ((LPC_I2C_T              *) LPC_I2C1_BASE)
#define LPC_I2C2                  ((LPC_I2C_T              *) LPC_I2C2_BASE)
#define LPC_I2S                   ((LPC_I2S_T              *) LPC_I2S_BASE)
#define LPC_QEI                   ((LPC_QEI_T              *) LPC_QEI_BASE)
#define LPC_DAC                   ((LPC_DAC_T              *) LPC_DAC_BASE)
#define LPC_ADC                   ((LPC_ADC_T              *) LPC_ADC_BASE)
#define LPC_IOCON                 ((LPC_IOCON_T            *) LPC_IOCON_BASE)
#define LPC_SYSCTL                ((LPC_SYSCTL_T           *) LPC_SYSCTL_BASE)
#define LPC_SYSCON                ((LPC_SYSCTL_T           *) LPC_SYSCTL_BASE) /* Alias for LPC_SYSCTL */
#define LPC_CANAF_RAM             ((LPC_CANAF_RAM_T        *) LPC_CANAF_RAM_BASE)
#define LPC_CANAF                 ((LPC_CANAF_T            *) LPC_CANAF_BASE)
#define LPC_CANCR                 ((LPC_CANCR_T            *) LPC_CANCR_BASE)
#define LPC_CAN1                  ((LPC_CAN_T              *) LPC_CAN1_BASE)
#define LPC_CAN2                  ((LPC_CAN_T              *) LPC_CAN2_BASE)
#define LPC_RITIMER               ((LPC_RITIMER_T          *) LPC_RITIMER_BASE)
#define LPC_FMC                   ((LPC_FMC_T              *) LPC_FMC_BASE)

/* IRQ Handler Alias list */
#define UART_IRQHandler           UART0_IRQHandler
#define I2C_IRQHandler            I2C0_IRQHandler
#define SSP_IRQHandler            SSP0_IRQHandler

/**
 * @}
 */

#include "sysctl_17xx_40xx.h"
#include "clock_17xx_40xx.h"
#include "iocon_17xx_40xx.h"
#include "adc_17xx_40xx.h"
#include "can_17xx_40xx.h"
#include "dac_17xx_40xx.h"
#include "enet_17xx_40xx.h"
#include "gpdma_17xx_40xx.h"
#include "gpio_17xx_40xx.h"
#include "gpioint_17xx_40xx.h"
#include "i2c_17xx_40xx.h"
#include "i2s_17xx_40xx.h"
#include "mcpwm_17xx_40xx.h"
#include "pmu_17xx_40xx.h"
#include "qei_17xx_40xx.h"
#include "ritimer_17xx_40xx.h"
#include "rtc_17xx_40xx.h"
#include "spi_17xx_40xx.h"
#include "ssp_17xx_40xx.h"
#include "timer_17xx_40xx.h"
#include "uart_17xx_40xx.h"
#include "usb_17xx_40xx.h"
#include "wwdt_17xx_40xx.h"
#include "fmc_17xx_40xx.h"
#include "romapi_17xx_40xx.h"
#include "pwm_17xx_40xx.h"

#ifdef __cplusplus
}
#endif

#endif /* __CHIP_LPC175X_6X_H_ */

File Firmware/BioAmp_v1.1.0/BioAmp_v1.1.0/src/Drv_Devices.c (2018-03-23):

/*
 * Drv_Devices.c
 *
 *  Created on: 6/11/2015
 *      Author: alumno
 */

#include "Drv_Devices.h"
#include "Drv_UART.h"
#include "Drv_ADS1299.h"
#include "Definitions_ADS1299.h"
#include "Drv_GPIO.h"
#include "board_api.h"
#include "chip.h"
#include <stdlib.h>

/**
 * @brief Flag to indicate if the ADS1299 is acquiring data or not
 */
bool is_running = FALSE;

/**
 * @brief Flag to indicate if channel settings commands are being received
 */
bool getChannelSettings = FALSE;

/**
 * @brief Mode of use: 8 or 16 channels
 */
uint8_t  outputType = OUTPUT_8_CHAN; //default to 8 channels

/**
 * @brief Counter to have control of the received commands
 */
uint8_t plusCounter = 0;

/**
 * @brief Auxiliary byte
 */
uint8_t testChar = 0;

/**
 * @brief Keep track of what channel we are loading settings for
 */
uint8_t currentChannelToSet = 0;

/**
 * @brief Counter used to retrieve channel settings from serial port
 */
uint8_t channelSettingsCounter = 0;

/**
 * @brief Flag to indicate the use of filters
 */
bool useFilters = FALSE;

/**
 * @brief Counter used to retrieve lead off settings from serial port
 */
uint8_t leadOffSettingsCounter = 0;

/**
 * @brief Flag to indicate if lead off settings commands are being received
 */
bool getLeadOffSettings = FALSE;

/**
 * @brief Flag to indicate if the board is Master (HIGH state) or Slave (LOW state)
 */
bool isMaster = FALSE;

/**
 * @brief Function for receiving new commands
 */
void Drv_Devices_eventSerial()
{
	uint8_t inChar = 0;

	while(Drv_UART_available())
	{
		inChar = Drv_UART_ReadByte();

		if(getChannelSettings) // if we just got an 'x' expect channel setting parameters
		{
			Drv_Devices_loadChannelSettings(inChar); //go get channel settings parameters
		}
		else if(getLeadOffSettings) // if we just got a 'z' expect lead-off setting parameters
		{
			Drv_Devices_loadLeadOffSettings(inChar); //go get lead-off settings parameters
		}
		else
		{
			Drv_Devices_getCommands(inChar); // decode the command
		}
	}

}
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

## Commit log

2017-05-14 Initial Hardware version
    [Biopotenciales_LIRINS-B.Cu.gbr, Biopotenciales_LIRINS-B.Mask.gbr, Biopotenciales_LIRINS-B.Paste.gbr, Biopotenciales_LIRINS-B.SilkS.gbr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]
2017-05-14 Cabinet desgin, initial version
    [bioamp_back_1.0.stl, bioamp_body_left_1.0.stl, bioamp_body_right_1.0.stl, bioamp_bottom_1.0.stl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]
2017-05-29 Hardware revision: Project filsytem for Kicad 4.0.6
    [BioAmp_v1.0.0-B.Cu.gbr, BioAmp_v1.0.0-B.Mask.gbr, BioAmp_v1.0.0-B.Paste.gbr, BioAmp_v1.0.0-B.SilkS.gbr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]
2017-05-29 Change folder name for Enclouser
    [bioamp_back_1.0.stl, bioamp_body_left_1.0.stl, bioamp_body_right_1.0.stl, bioamp_bottom_1.0.stl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]
2017-06-05 Fix a typo on a folder name
    [bioamp_back_1.0.stl, bioamp_body_left_1.0.stl, bioamp_body_right_1.0.stl, bioamp_bottom_1.0.stl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]
2017-06-05 Update folder tree
    [bioamp_back_1.0.stl, bioamp_body_left_1.0.stl, bioamp_body_right_1.0.stl, bioamp_bottom_1.0.stl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]
2017-07-10 Update Hardware/Bioamp_v1.0.0: Project Folders Tree
    [BioAmp_v1.0.0-B.Cu.gbr, BioAmp_v1.0.0-B.Mask.gbr, BioAmp_v1.0.0-B.Paste.gbr, BioAmp_v1.0.0-B.SilkS.gbr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]
2017-07-10 Update Hardware/Bioamp_v1.0.0_DB: Project Folder Tree
    [BioAmp_v1.0.0_DB-B.Cu.gbr, BioAmp_v1.0.0_DB-B.Mask.gbr, BioAmp_v1.0.0_DB-B.Paste.gbr, BioAmp_v1.0.0_DB-B.SilkS.gbr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]
2017-07-10 Update Hardware/3D_boards: Models
    [BioAmp_v1_0_0.FCStd, BioAmp_v1_0_0_DB.FCStd]
2017-09-06 New enclosure version v1.2. Better assembly for parts.
    [bioamp_back_1.2.stl, bioamp_body_left_1.2.stl, bioamp_body_right_1.2.stl, bioamp_bottom_1.2.stl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]
2018-03-22 Remove Hardware V1.0.0
    [BioAmp_v1.0.0-B.Cu.gbr, BioAmp_v1.0.0-B.Mask.gbr, BioAmp_v1.0.0-B.Paste.gbr, BioAmp_v1.0.0-B.SilkS.gbr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]
2018-03-22 Upgrade to hardware v1.1.0: Isolated inputs for events record
    [BioAmp_v1.1.0-B.Cu.gbr, BioAmp_v1.1.0-B.Mask.gbr, BioAmp_v1.1.0-B.Paste.gbr, BioAmp_v1.1.0-B.SilkS.gbr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]
2018-08-24 Se remueve la versión inicial del Manual de Usuario
2018-08-24 Se actualiza el Manual de Usuario
2018-08-24 Se incorpora una Guia rápida de instalación y uso
2018-08-24 Se actualiza la estructura de la carpeta Hardware
